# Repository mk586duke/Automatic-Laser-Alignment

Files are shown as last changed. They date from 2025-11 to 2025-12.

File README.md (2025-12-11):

# Automatic Laser Alignment
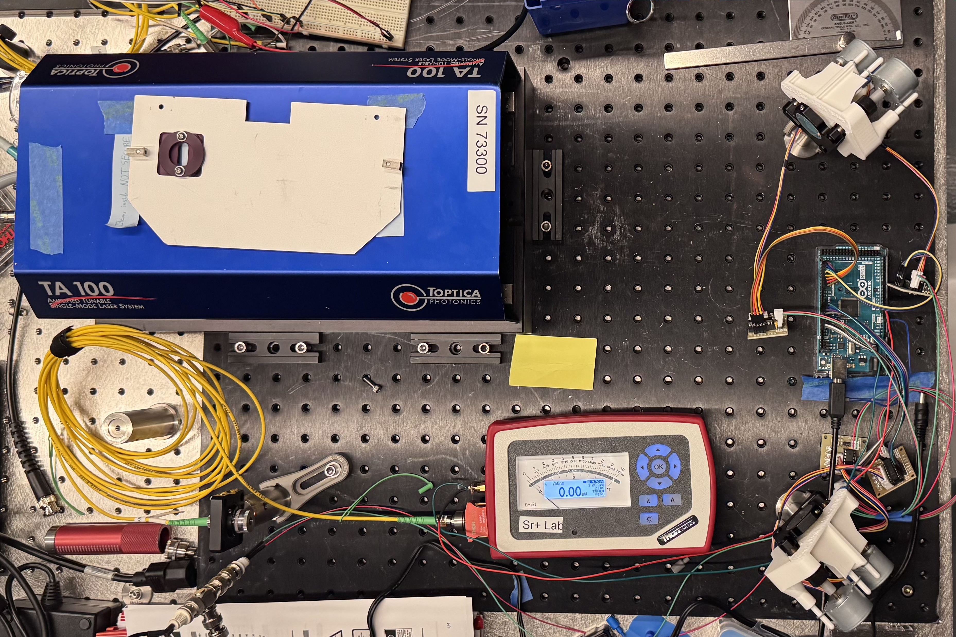
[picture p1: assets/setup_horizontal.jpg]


## Introduction
This project implements an automated retrofittable laser alignment system designed to optimize optical coupling efficiency for optical setups in a general physics laboratory environment, such as experiments at the Duke Quantum Center.

Traditionally, coupling laser beams into fibers is a labor-intensive and manual process that can take hours and suffer from inconsistency. Furthermore, such an alignment is not permanent, and due to factors such as human error, addition of new components, or simply mechanical drift, alignment needs to be repeated constantly for a single laser path. Considering the large number of such paths for just a single experimental setup, the combined hours of labor are significant.

There exist solutions for this problem in the market, which are prepackaged motorized mirror mounts and controllers. However, these devices are expensive and are also entirely new parts that cannot be immediately applied to an existing optical path. Considering the sheer number of mirror mounts used in a system, the cost and hours necessary for setting these devices up become prohibitive.

We present a solution that is both inexpensive and retrofittable. Our solution automates a 4-axis alignment task using a Nelder-Mead optimization algorithm running on an Arduino Mega. By controlling motorized mirror mounts, the system achieves high-precision alignment in minutes with superior repeatability compared to manual methods.

## System Specifications
### Targeting accuracy goals:
-  Lateral error ≤ ± 250 μm
-  Angular error ≤ ± 5 mrad
### Performance goals:
-  System improves output power relative to misaligned start
-  Manual override available at any time
-  Typical alignment cycle completes within a few to tens of minutes
- System is easy to install onto the prexisting hardware
## Design Description
### Software Architecture

The core logic resides in `arduino_full.ino`, which implements the control loop and optimization algorithm.
- **Optimization Algorithm**: A custom C++ implementation of the **Nelder-Mead simplex method** (`nelderMead4D`). It optimizes a 4-dimensional space (X/Y axes for 2 mirrors) to maximize light intensity. One convenient part of this method is that it requires very little prior information. No gradients are used and the function is agnostic to the underlying intensity profile or motor identifiers.
- **Motor Control**: The `setMirrorPositions` function manages four `Stepper` objects (using the standard Arduino `Stepper.h` library). It handles coordinate tracking and sequential motor movement. Gear ratios and step sizes are defined in constants at the top of the file.
- **Sensor Interface**: The `measureIntensity` function reads the analog voltage from the photodetector (pin A0), averaging multiple samples (`ADC_SAMPLES`) to reduce noise.
- **Simulation Mode**: A `SIMULATED` flag allows testing the optimization logic without physical hardware by using a mathematical model of the laser intensity profile.

### Hardware Architecture
#### Pre-Existing Hardware Setup

The hardware setup for the automatic laser alignment system includes the following components.
- One laser source (Diode @760nm in TA100)
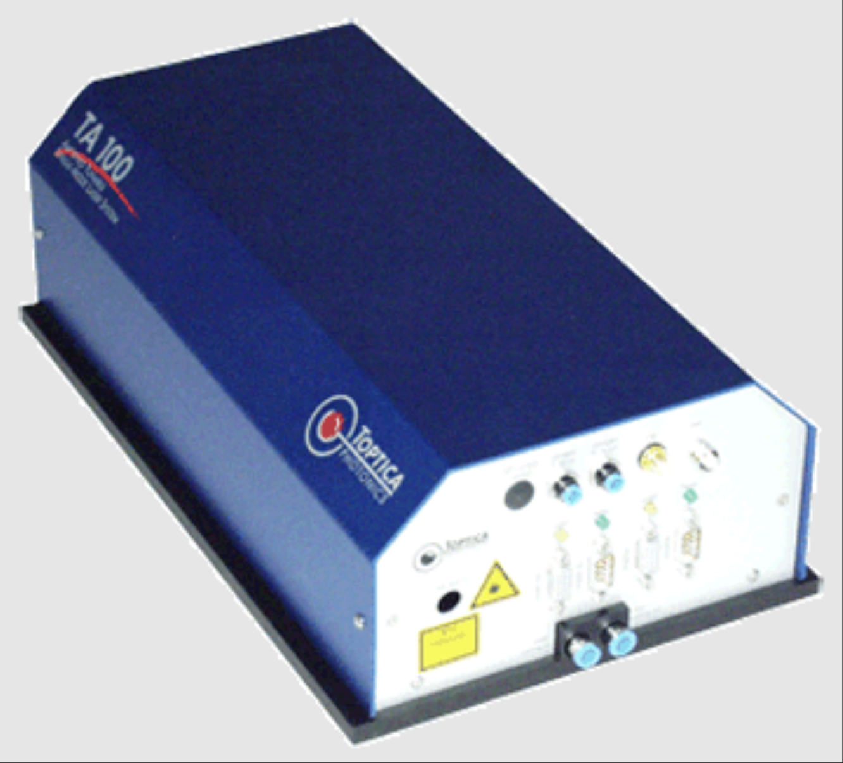
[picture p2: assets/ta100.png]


- Two 2-axis mirror mounts (K100) with installed mirrors

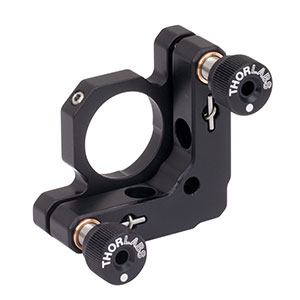
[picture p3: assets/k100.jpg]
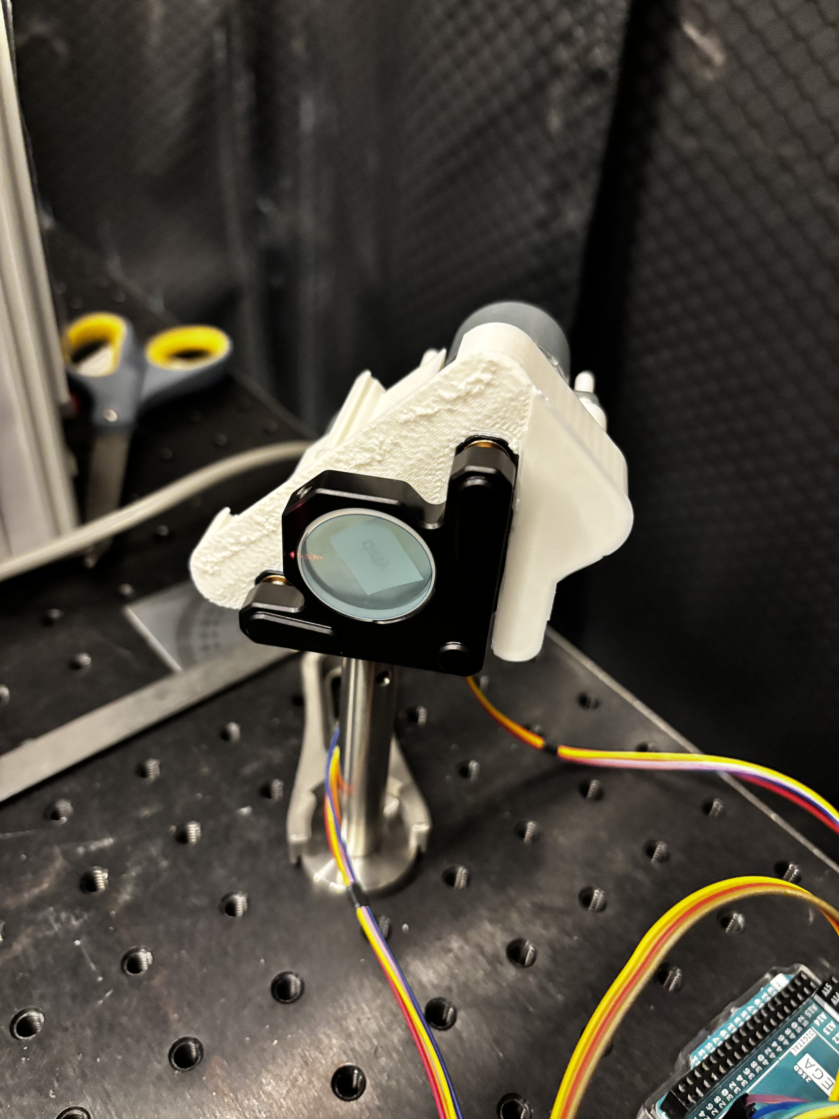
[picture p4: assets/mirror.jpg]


- One (mounted) collimator (CFC11A) and fiber

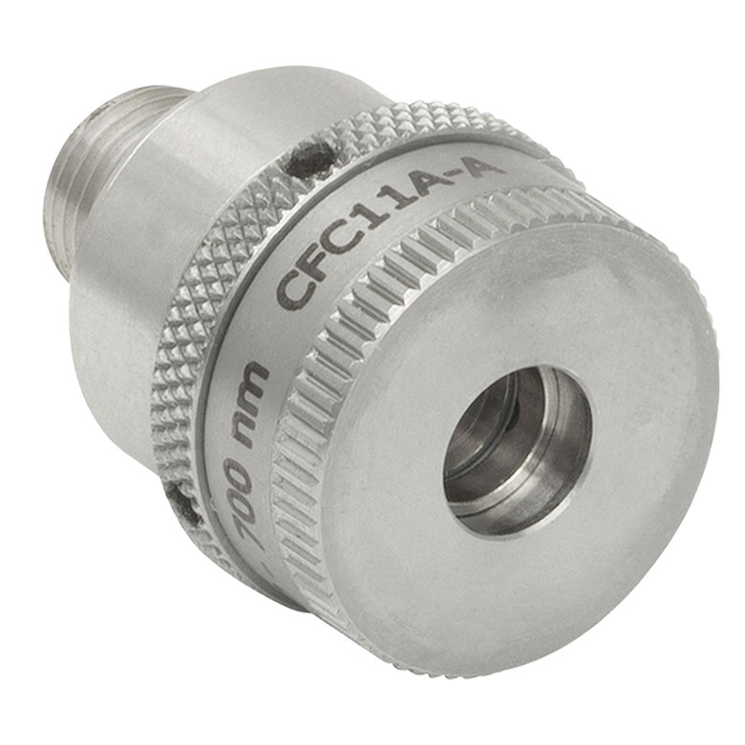
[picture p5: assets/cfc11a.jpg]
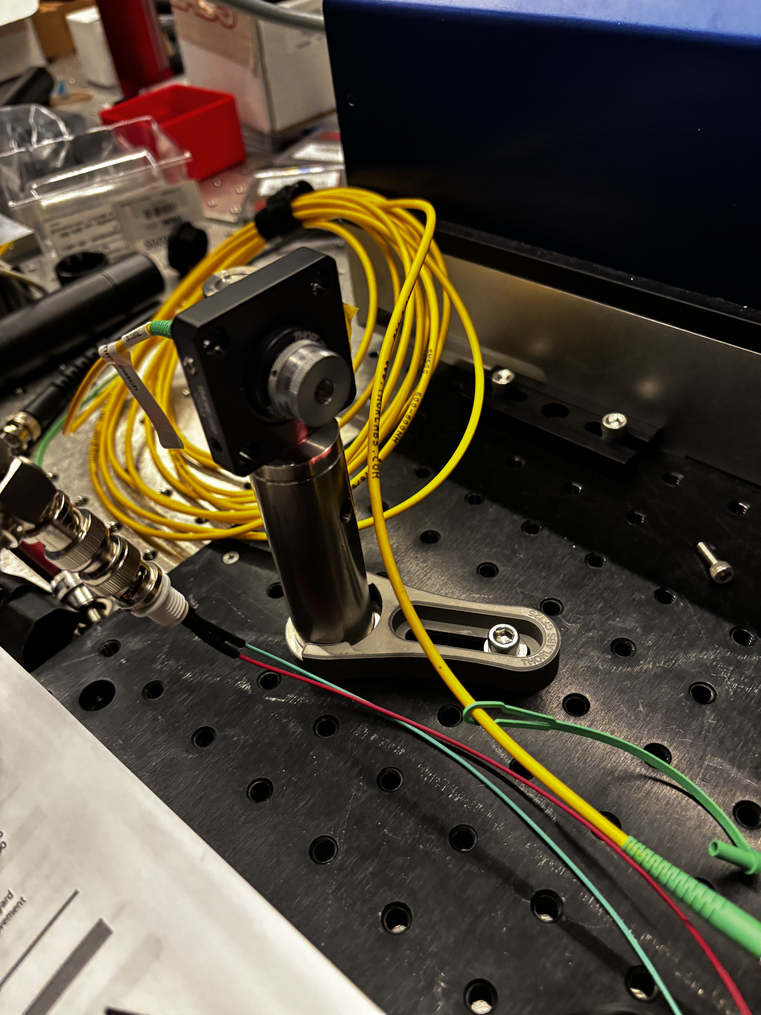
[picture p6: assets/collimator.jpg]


- One power meter (Thorlabs PM100A)
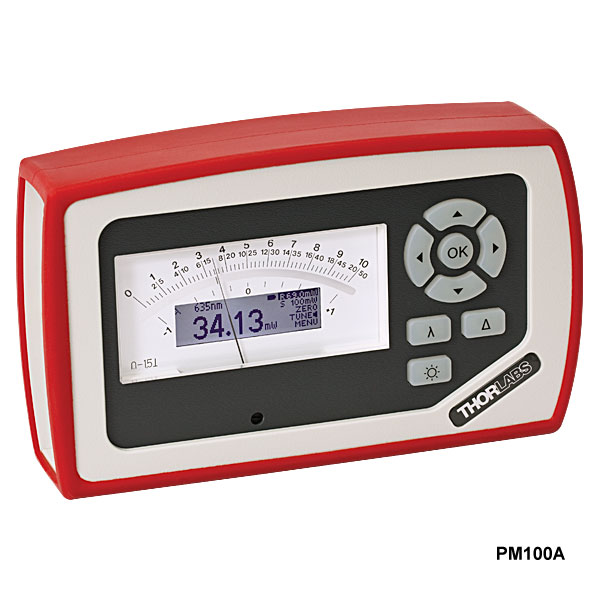
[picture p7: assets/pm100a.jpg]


#### New Components
The hardware setup consists of the following components:
- Four 2048-step stepper motors (28BYJ-48) to control two 2-axis mirrors
- Four motor drivers (ULN2003)
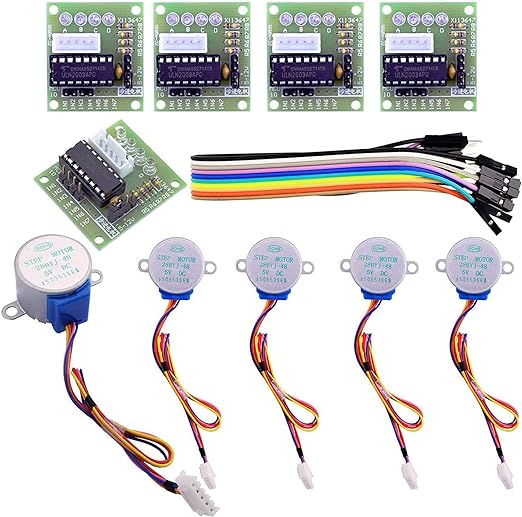
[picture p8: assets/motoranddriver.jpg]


- Two motor holding and guidance assemblies (designed, 3D print)
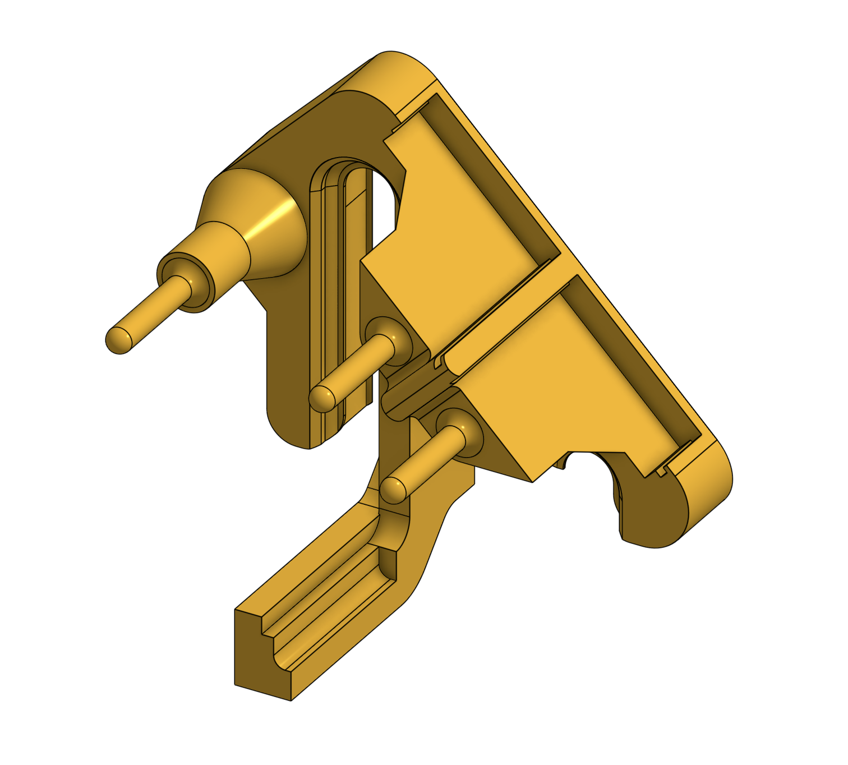
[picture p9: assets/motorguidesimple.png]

- Four motor-screw adaptors (designed, 3D print)
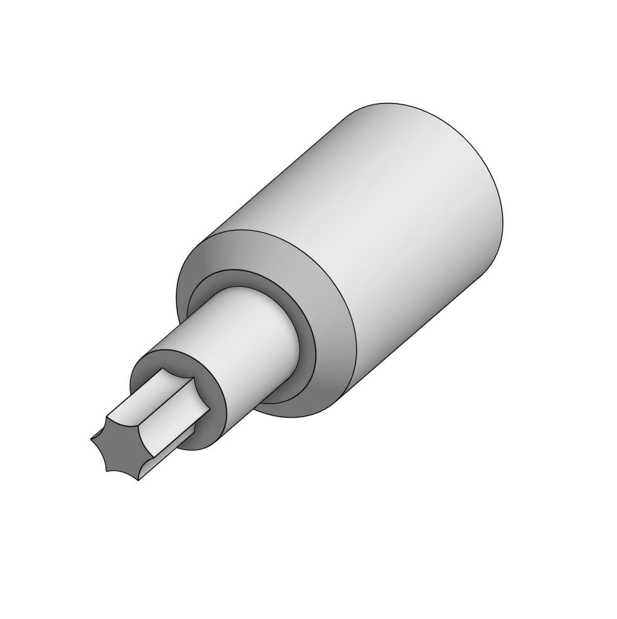
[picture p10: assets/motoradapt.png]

- One microcontroller board (Arduino Mega 2560) to control the stepper motors and read photodetector values
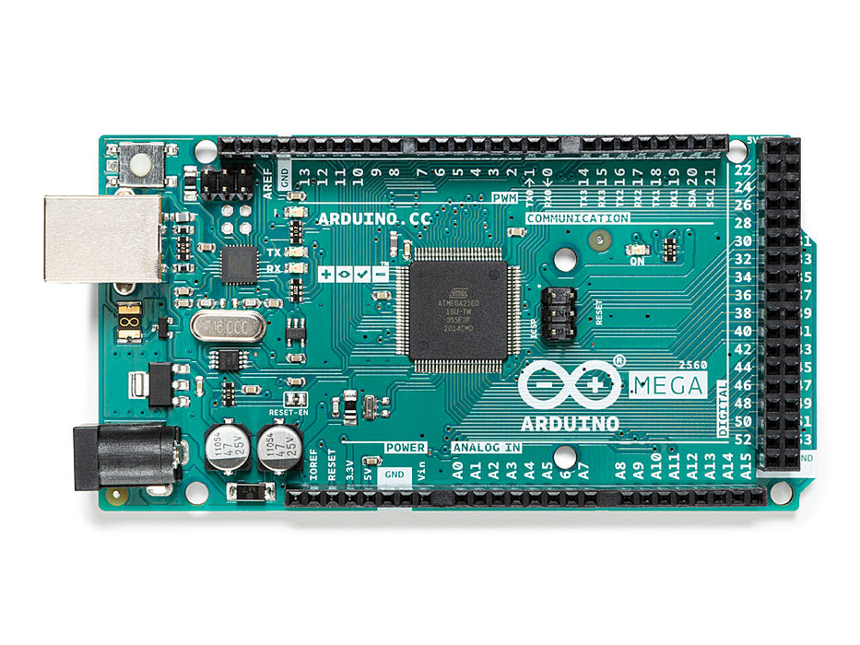
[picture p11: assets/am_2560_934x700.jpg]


#### Power and Networking
- The photodetector outputs an analog voltage proportional to the detected light intensity. This signal is transmitted to the Arduino Mega via analog input pin A0.
- The stepper motors communicate with the Arduino Mega through its corresponding motor driver board, which interprets and converts the control signal from the Arduino Mega. It also draws power to drive the motor.
- All power used in the new components comes from one 5V power supply from the wall. Total operating current does not exceed 2A for a 4-motor setup.

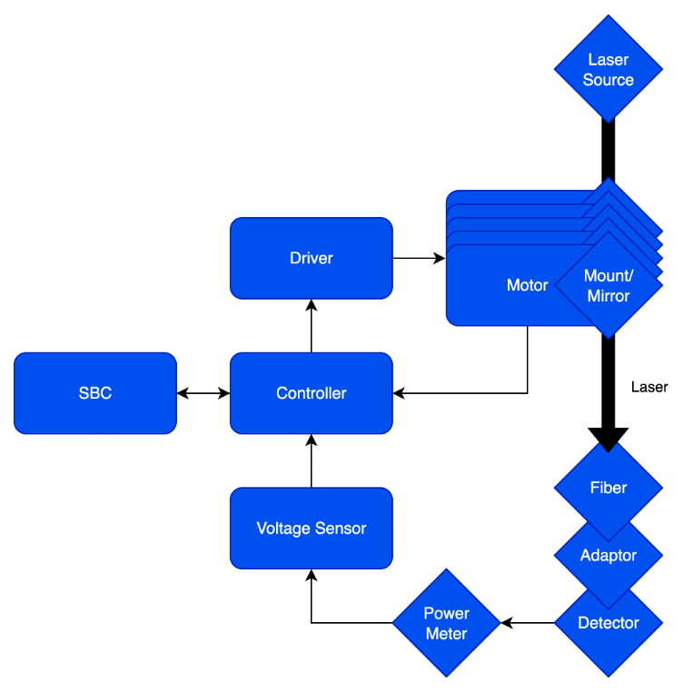
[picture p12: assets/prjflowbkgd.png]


## Testing and Validation
### Targeting accuracy:
-  Lateral error ≤ ± 250 μm
-  Angular error ≤ ± 5 mrad

####  Theoretical Resolution
Based on the hardware specifications defined in the firmware (`arduino_full.ino`), we can calculate the theoretical mechanical resolution of the system.

*   **Stepper Motor**: 2048 steps per revolution (28BYJ-48).
*   **Mirror Mount Gearing**: 2 motor revolutions per 1 degree of mirror tilt (`REV_PER_DEGREE`).
*   **System Steps per Degree**: $2048 \times 2 = 4096$ steps/degree.

**Angular Resolution**:

$\theta_{res} = \frac{1}{4096} \approx 0.000244^\circ \approx 4.26 \mu\text{rad}$

**Lateral Resolution**:

At a target distance of 50 cm, the theoretical beam displacement per step is:

$\Delta x = d \times \tan(\theta_{res}) \approx 500 \text{ mm} \times 4.26 \times 10^{-6} \approx 2.13 \mu\text{m}$

#### Practical Demonstration of Targeting Accuracy
We demonstrated the upper-bound targeting error by doing full rotations of the motor back and forth, showing sub-mm lateral error over the course of 4096 steps (1 degree of mirror motion).

*Video demonstration available in assets/demovids/emperical_demo.mp4*

### Performance goals:
- [x]  System improves output power relative to misaligned start: We consistently observed a significant increase in detected intensity after running the alignment routine from various misaligned starting positions. The determinism of the stepper motors ensured non-decreasing performance across multiple trials & we achieved consistent improvements, comparable to human tuning.
- [x]  Manual override available at any time: System could be reset with a single button press on the Arduino Mega. During alignment, manual adjustments to the mirror mounts were possible without damaging the motors or losing system state. Additionally, all components went through a single 5V power supply, simplifying the wiring and making deactivation straightforward.
- [x]  Typical alignment cycle completes within a few to tens of minutes: Alignment convergence consistently in 1-3 minutes.
- [x]  System is easy to install onto the preexisting hardware: All components were either extremely common (Arduino Mega, 28BYJ-48 stepper motors) or 3d-printable. The entire system was assembled on a standard optical table using common mounting hardware (posts, post holders, breadboards). Our motor mount slid onto the K100 mirror mounts without modification and we would repeatably take the system on and off the optical table without issue during testing.

## Demonstration Videos
The demonstration videos showcasing the fully working system can be found in the assets/videos folder or should be attached in the email along with this document.

*Note that demo1.mp4 shows alignment where the laser has a high power setting

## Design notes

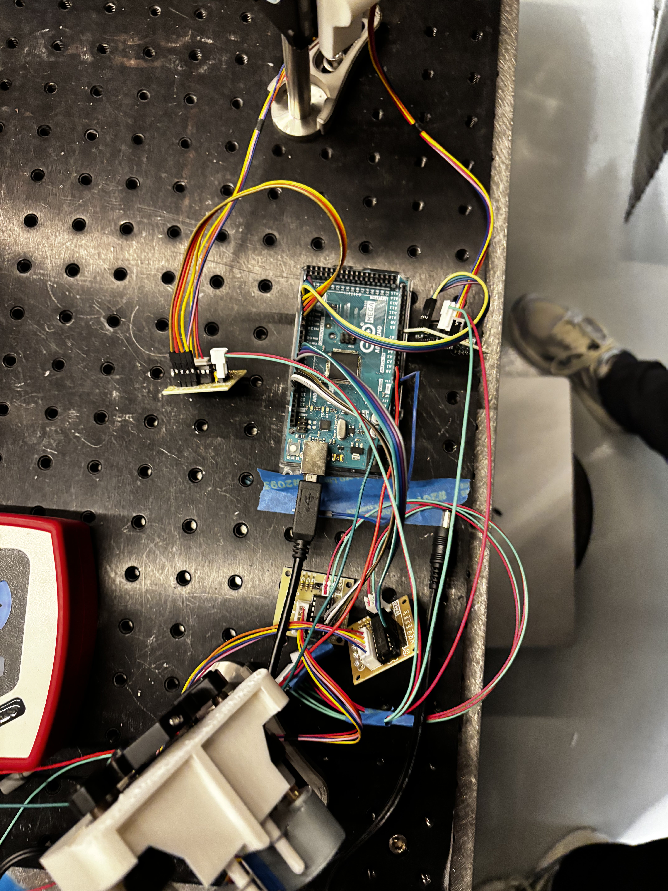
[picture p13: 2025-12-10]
assets/computers.jpg

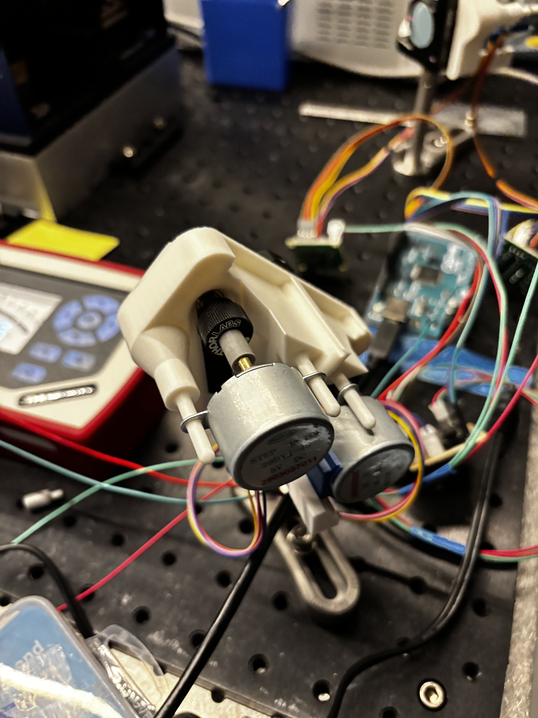
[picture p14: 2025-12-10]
assets/stepper.jpg

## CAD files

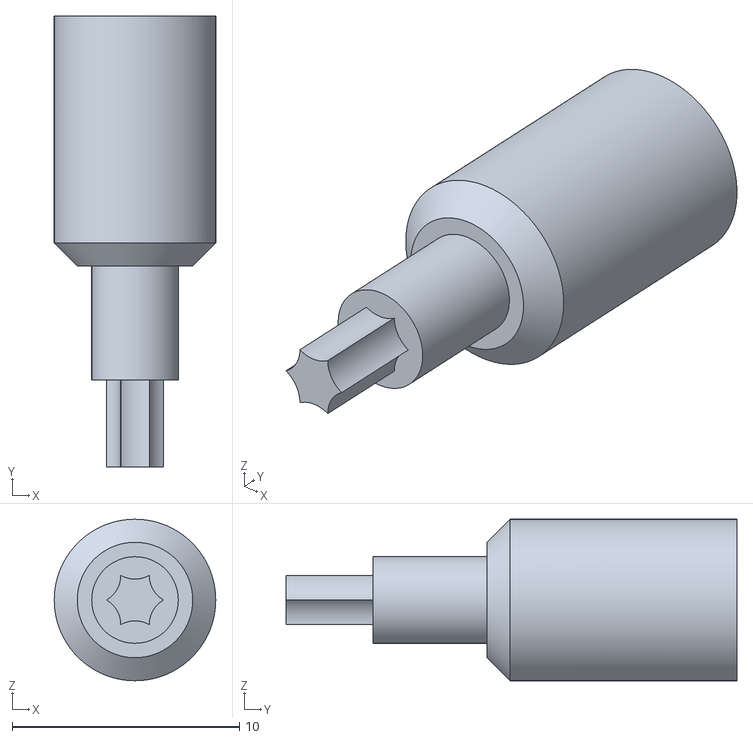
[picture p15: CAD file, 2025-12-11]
assets/models/Motor Adaptor M - Part 10.stl
7.11 x 19.9 x 7.11

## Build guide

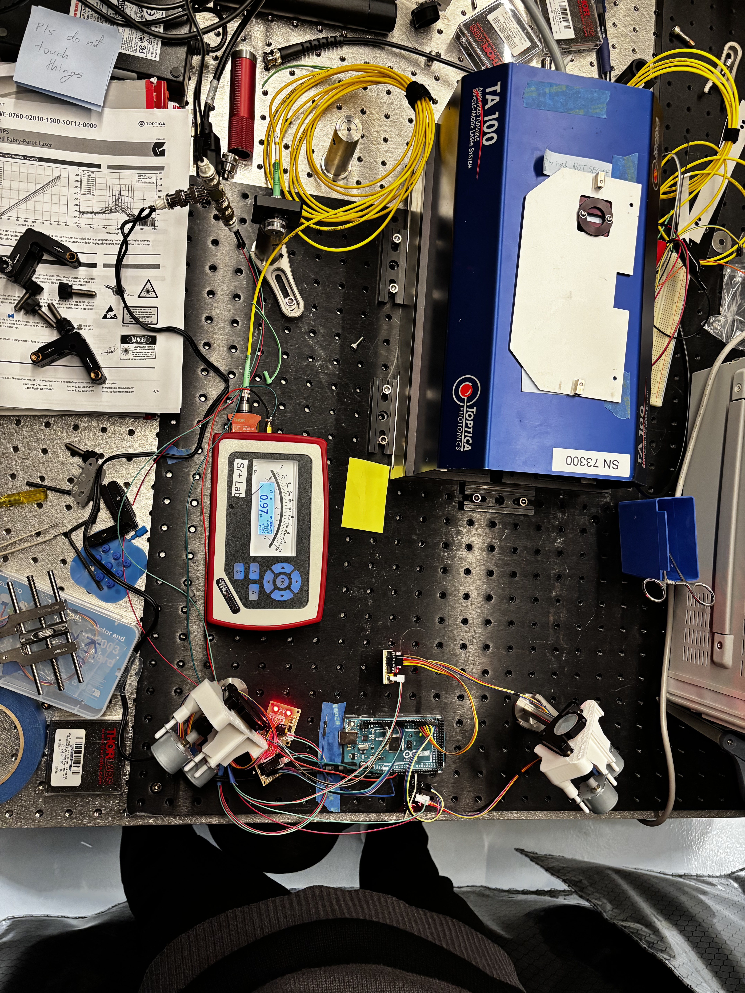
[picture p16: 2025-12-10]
assets/setup_top.jpg

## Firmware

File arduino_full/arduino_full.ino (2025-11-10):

/*
 * Arduino Nelder–Mead 3D Laser Alignment Optimizer
 * Controls four 2048-step steppers (e.g., 28BYJ-48) for two 2-axis mirrors.
 * Uses 4D Nelder-Mead optimization to find mirror angles that maximize 
 * laser coupling intensity into a fiber optic or photodetector.
 * 
 * Hardware:
 * - 4x Stepper motors (28BYJ-48 with ULN2003 drivers)
 * - 1x Photodetector (analog output on A0)
 * - 2x Gimbal-mounted mirrors (2 steppers each for X/Y control)
 * 
 * Optimization:
 * - Algorithm: Nelder-Mead simplex method (derivative-free)
 * - Dimensions: 4D (ax1, ay1, ax2, ay2)
 * - Typical convergence: 50-200 iterations
 */

#include <Arduino.h>
#include <Stepper.h>

/* ------------------- CONFIGURATION ------------------- */

// Stepper configuration
#define STEPS_PER_REV 2048
#define REV_PER_DEGREE 2   // Product page lists 0.5º per revolution or 2 rev/degree

// Stepper pin mapping TODO: need to adjust this to fit the physical board
Stepper stepper_m1x(STEPS_PER_REV, 8, 10, 9, 11);
Stepper stepper_m1y(STEPS_PER_REV, 4, 6, 5, 7);
Stepper stepper_m2x(STEPS_PER_REV, 22, 24, 23, 25);
Stepper stepper_m2y(STEPS_PER_REV, 18, 20, 19, 21);

static long stepper_m1x_current_pos = 0;
static long stepper_m1y_current_pos = 0;
static long stepper_m2x_current_pos = 0;
static long stepper_m2y_current_pos = 0;

// Sensor input
#define SENSOR_PIN A0
#define ADC_SAMPLES 8
#define SETTLE_DELAY_MS 50

// Optimization parameters (in steps)
#define INITIAL_STEP_SIZE_STEPS 100        // initial simplex step size (motor steps)
#define MAX_ITERATIONS 500
#define REFLECTION_COEFFICIENT 1.0         // alpha: reflection
#define EXPANSION_COEFFICIENT 2.0          // gamma: expansion
#define CONTRACTION_COEFFICIENT 0.5        // rho: contraction
#define SHRINK_COEFFICIENT 0.5             // sigma: shrink
#define FUNCTION_TOLERANCE 1e-8            // Very tight convergence criterion
#define PARAMETER_TOLERANCE 1.0            // tolerance in steps

// Testing mode
bool SIMULATED = false;  // Set to true to use simulated intensity (no motor movement)

/* ------------------- MIRROR / STEPPER UTILS ------------------- */

/**
 * Move a single stepper motor to a target position in steps.
 * 
 * Calculates the relative movement needed from the current position,
 * executes the move, and updates the position tracker. 
 * Note: stepper.step() is BLOCKING and will halt execution until complete.
 * 
 * @param stepper Reference to the Stepper object to control
 * @param current_position Reference to the position tracker (will be updated)
 * @param target_steps Target position in motor steps
 */
void setMirrorPosition(Stepper &stepper, long &current_position, long target_steps) {
  long step_difference = target_steps - current_position;
  stepper.step(step_difference);
  current_position = target_steps;
}

/**
 * Move all four stepper motors to their target positions.
 * 
 * Controls the X and Y axes for both mirrors (M1 and M2) by moving each
 * stepper motor sequentially. Motors move one at a time (not simultaneously)
 * due to the blocking nature of the Stepper library.
 * 
 * @param mirror1_x_steps Mirror 1 X-axis position in steps
 * @param mirror1_y_steps Mirror 1 Y-axis position in steps
 * @param mirror2_x_steps Mirror 2 X-axis position in steps
 * @param mirror2_y_steps Mirror 2 Y-axis position in steps
 */
void setMirrorPositions(long mirror1_x_steps, long mirror1_y_steps, 
                        long mirror2_x_steps, long mirror2_y_steps) {
  if (SIMULATED) {
    // In simulation mode, just update position trackers without moving motors
    stepper_m1x_current_pos = mirror1_x_steps;
    stepper_m1y_current_pos = mirror1_y_steps;
    stepper_m2x_current_pos = mirror2_x_steps;
    stepper_m2y_current_pos = mirror2_y_steps;
    return;
  }
  
  setMirrorPosition(stepper_m1x, stepper_m1x_current_pos, mirror1_x_steps);
  setMirrorPosition(stepper_m1y, stepper_m1y_current_pos, mirror1_y_steps);
  setMirrorPosition(stepper_m2x, stepper_m2x_current_pos, mirror2_x_steps);
  setMirrorPosition(stepper_m2y, stepper_m2y_current_pos, mirror2_y_steps);
}

/* ------------------- MEASUREMENT ------------------- */

/**
 * Measure light intensity at a given mirror configuration.
 * 
 * Moves all four mirrors to the specified positions, waits for mechanical settling,
 * then takes multiple ADC readings from the photodetector and returns their
 * average. Higher values indicate brighter light (better alignment).
 * 
 * @param mirror1_x_steps Mirror 1 X-axis position in steps
 * @param mirror1_y_steps Mirror 1 Y-axis position in steps
 * @param mirror2_x_steps Mirror 2 X-axis position in steps
 * @param mirror2_y_steps Mirror 2 Y-axis position in steps
 * @return Average ADC reading (0-1023 for 10-bit ADC), normalized to [0, 1]
 */
double measureIntensity(long mirror1_x_steps, long mirror1_y_steps, 
                        long mirror2_x_steps, long mirror2_y_steps) {
  if (SIMULATED) {
    return simulatedMeasureIntensity(mirror1_x_steps, mirror1_y_steps, 
                                      mirror2_x_steps, mirror2_y_steps);
  }
  
  setMirrorPositions(mirror1_x_steps, mirror1_y_steps, mirror2_x_steps, mirror2_y_steps);
  delay(SETTLE_DELAY_MS);

  long sum = 0;
  for (int i = 0; i < ADC_SAMPLES; i++) {
    sum += analogRead(SENSOR_PIN);
  }
  double average = (double)sum / ADC_SAMPLES;
  return average / 1023.0; // Normalize to [0, 1]
}

double simulatedMeasureIntensity(long m1x, long m1y, long m2x, long m2y) {
  // Simulated "optimal" positions (in steps)
  const long OPTIMAL_M1X = 500;
  const long OPTIMAL_M1Y = 300;
  const long OPTIMAL_M2X = 700;
  const long OPTIMAL_M2Y = 400;

  // Calculate squared distance from optimal
  long dx = m1x - OPTIMAL_M1X;
  long dy = m1y - OPTIMAL_M1Y;
  long dz = m2x - OPTIMAL_M2X;
  long dw = m2y - OPTIMAL_M2Y;
  long distance_squared = dx*dx + dy*dy + dz*dz + dw*dw;

  // Simulated intensity: max at optimal, decreases with distance
  double intensity = exp(-0.0001 * distance_squared); // Gaussian falloff
  return intensity;
}

/* ------------------- SIMPLE UTILS ------------------- */

/**
 * Copy values from one vector to another.
 * 
 * Simple utility for vector operations in the Nelder-Mead algorithm.
 * 
 * @param destination Destination array pointer
 * @param source Source array pointer
 * @param num_elements Number of elements to copy
 */
void copyVector(double *destination, const double *source, int num_elements) {
  for (int i = 0; i < num_elements; i++) {
    destination[i] = source[i];
  }
}

/**
 * Calculate the centroid of n points in N-dimensional space.
 * 
 * Used in the Nelder-Mead algorithm to find the center of the best n
 * vertices of the simplex before performing reflection/expansion operations.
 * 
 * @param centroid Output: centroid coordinates
 * @param points Array of n points, each with dimensions
 * @param num_points Number of points
 * @param dimensions Dimensionality of each point
 */
void calculateCentroid(double *centroid, double **points, int num_points, int dimensions) {
  for (int dimension = 0; dimension < dimensions; dimension++) {
    centroid[dimension] = 0.0;
    for (int i = 0; i < num_points; i++) {
      centroid[dimension] += points[i][dimension];
    }
    centroid[dimension] /= (double)num_points;
  }
}

/* ------------------- NELDER–MEAD (4D) ------------------- */

/**
 * Nelder-Mead optimization algorithm for 4D parameter space (in motor steps).
 * 
 * A derivative-free optimization method that uses a simplex (5 points in 4D)
 * to iteratively search for the motor positions (in steps) that maximize light intensity.
 * The algorithm reflects, expands, contracts, or shrinks the simplex based on
 * function evaluations at each vertex.
 * 
 * The algorithm minimizes -intensity (equivalent to maximizing intensity).
 * Operations performed at each iteration:
 * - Reflection: Try a point mirrored across the centroid from the worst point
 * - Expansion: If reflection is good, try going further in that direction
 * - Contraction: If reflection is bad, try a point between centroid and worst
 * - Shrink: If contraction fails, pull all points toward the best point
 * 
 * @param initial_guess Initial guess for parameters [m1x, m1y, m2x, m2y] in steps
 * @param step_size Initial simplex size in steps
 * @param max_iterations Maximum number of iterations before termination
 * @param function_tolerance Function value tolerance for convergence (checks std dev of function values)
 * @param parameter_tolerance Parameter tolerance for convergence (currently unused)
 * @param best_parameters_out Output: best parameters found [m1x, m1y, m2x, m2y] in steps
 * @param best_intensity_out Output: best intensity value achieved
 */
void nelderMead4D(long initial_guess[4], long step_size, int max_iterations,
                  double function_tolerance, double parameter_tolerance,
                  long best_parameters_out[4], double *best_intensity_out) {

  const int NUM_DIMENSIONS = 4;
  const int NUM_VERTICES = NUM_DIMENSIONS + 1;  // 5 vertices for 4D simplex

  // Simplex vertices (5 points in 4D) - using doubles for intermediate calculations
  double simplex_vertices[NUM_VERTICES][NUM_DIMENSIONS];              // The coordinates of each vertex
  double function_values[NUM_VERTICES];                               // The function values at each vertex

  // Build initial simplex using regular simplex construction
  // Vertex 0: initial guess
  for (int dimension = 0; dimension < NUM_DIMENSIONS; dimension++) {
    simplex_vertices[0][dimension] = (double)initial_guess[dimension];
  }
  
  // Vertices 1-4: perturb each dimension
  for (int vertex = 1; vertex <= NUM_DIMENSIONS; vertex++) {
    for (int dimension = 0; dimension < NUM_DIMENSIONS; dimension++) {
      simplex_vertices[vertex][dimension] = (double)initial_guess[dimension];
    }
    simplex_vertices[vertex][vertex-1] += (double)step_size;  // Perturb dimension vertex-1
  }

  // Measure initial points
  for (int vertex = 0; vertex < NUM_VERTICES; vertex++) {
    function_values[vertex] = -measureIntensity(
      lround(simplex_vertices[vertex][0]), 
      lround(simplex_vertices[vertex][1]), 
      lround(simplex_vertices[vertex][2]), 
      lround(simplex_vertices[vertex][3])
    ); // negative => minimize
  }

  int iteration = 0;
  while (iteration < max_iterations) {
    // Sort vertices by function_values ascending (best first)
    for (int i = 0; i < NUM_VERTICES - 1; i++) {
      for (int j = i + 1; j < NUM_VERTICES; j++) {
        if (function_values[j] < function_values[i]) {
          double temp_value = function_values[i]; 
          function_values[i] = function_values[j]; 
          function_values[j] = temp_value;
          
          double temp_vertex[NUM_DIMENSIONS]; 
          copyVector(temp_vertex, simplex_vertices[i], NUM_DIMENSIONS);
          copyVector(simplex_vertices[i], simplex_vertices[j], NUM_DIMENSIONS); 
          copyVector(simplex_vertices[j], temp_vertex, NUM_DIMENSIONS);
        }
      }
    }

    // Compute centroid of best n points (exclude worst)
    double centroid[NUM_DIMENSIONS];
    double *best_points[NUM_DIMENSIONS];
    for (int i = 0; i < NUM_DIMENSIONS; i++) {
      best_points[i] = simplex_vertices[i];
    }
    calculateCentroid(centroid, best_points, NUM_DIMENSIONS, NUM_DIMENSIONS);

    // Reflection
    double reflected_point[NUM_DIMENSIONS];
    for (int dimension = 0; dimension < NUM_DIMENSIONS; dimension++) {
      reflected_point[dimension] = centroid[dimension] + 
        REFLECTION_COEFFICIENT * (centroid[dimension] - simplex_vertices[NUM_VERTICES-1][dimension]);
    }
    double reflected_value = -measureIntensity(
      lround(reflected_point[0]), lround(reflected_point[1]), 
      lround(reflected_point[2]), lround(reflected_point[3])
    );
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

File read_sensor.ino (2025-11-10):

/*
 * Simple Analog Sensor Reader
 * Reads from pin A0 and prints the value to Serial
 */

#define SENSOR_PIN A0
#define BAUD_RATE 9600
#define SAMPLE_DELAY_MS 100  // Delay between readings (100ms = 10 readings/sec)

void setup() {
  Serial.begin(BAUD_RATE);
  analogReference(DEFAULT);
  
  delay(1000);
  Serial.println("Analog Sensor Reader");
  Serial.println("Reading from pin A0");
  Serial.println("Value range: 0-1023 (10-bit ADC)");
  Serial.println("---");
}

void loop() {
  int raw_value = analogRead(SENSOR_PIN);
  double voltage = (raw_value / 1023.0) * 5.0;  // Assuming 5V reference
  
  Serial.print("Raw: ");
  Serial.print(raw_value);
  Serial.print(" | Voltage: ");
  Serial.print(voltage, 3);
  Serial.println(" V");
  
  delay(SAMPLE_DELAY_MS);
}

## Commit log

2025-10-30 Add simple.c for stepper motor control
2025-11-06 arduino code
2025-12-11 No stl
    This README introduces an automated laser alignment system, detailing its purpose, specifications, design, and testing results.
2025-12-11 Embed 3D model in README
    Added a script tag to embed a 3D model of the motor guide.
